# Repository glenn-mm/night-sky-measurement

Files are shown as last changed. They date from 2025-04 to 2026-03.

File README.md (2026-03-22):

# night-sky-measurement
Build and code for optical night sky measurements

Calibration will require the use of an SQM-L device from https://www.unihedron.com/projects/sqm-l/

## Build Steps:
1. Solder the pins onto the QtPy
2. Connect the uFL antenna to the QtPy
3. Connect TSL2591 via STEMMA cable to QtPy
4. Solder the pins onto the display
5. Download Thonny (https://thonny.org)
6. Install Circuit Python onto QtPy via Thonny (put chp into boot mode first!)
7. Download Circuit Python libraries (https://circuitpython.org/libraries)
8. Add necessary libraries to Circuit Python drive under lib directory
   * adafruit_bus_device
   * adafruit_tsl2591.mpy
   * adafruit_displayio_ssd1306.mpy
   * adafruit_ssd1306.mpy
   * adafruit_display_text
9. Run example from https://github.com/adafruit/Adafruit_CircuitPython_TSL2591/blob/main/examples/tsl2591_simpletest.py
10. Copy code.py from this project and test display and sensor
11. Package into case
12. Calibrate
13. Bonus - connection to wifi + adafruit.io

## Build Steps explained:

### Breadboard layout (1)
* This picture shows the nomimal layout of the breadboard to get started
* Start by pressing the QtPy headers into the rows shown and soldering the QtPy to the headers

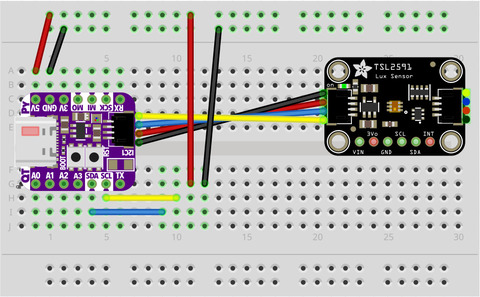
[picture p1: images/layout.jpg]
Fritzing breadboard layout


### QtPy with antenna (2)
* The uFL antenna is tricky to connect and requires a decent amount of force
* After soldering the QtPy to the headers on a breadboard verify the antenna connects

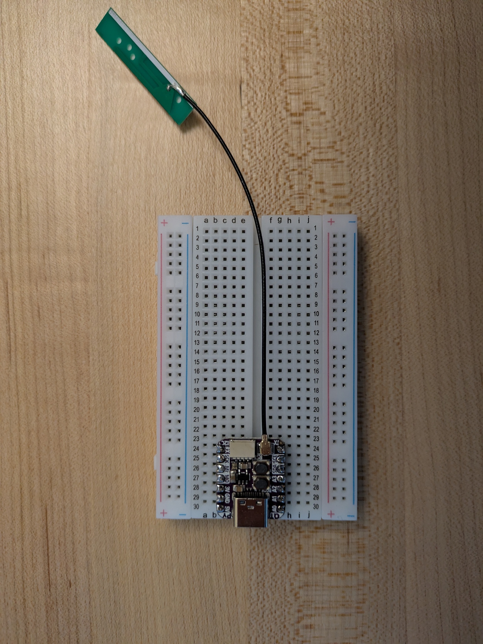
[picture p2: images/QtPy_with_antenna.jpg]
QtPy with antenna


### Attach TSL2591 (3)
* Attach the TSL2591 sensor via the STEMMA QT cable

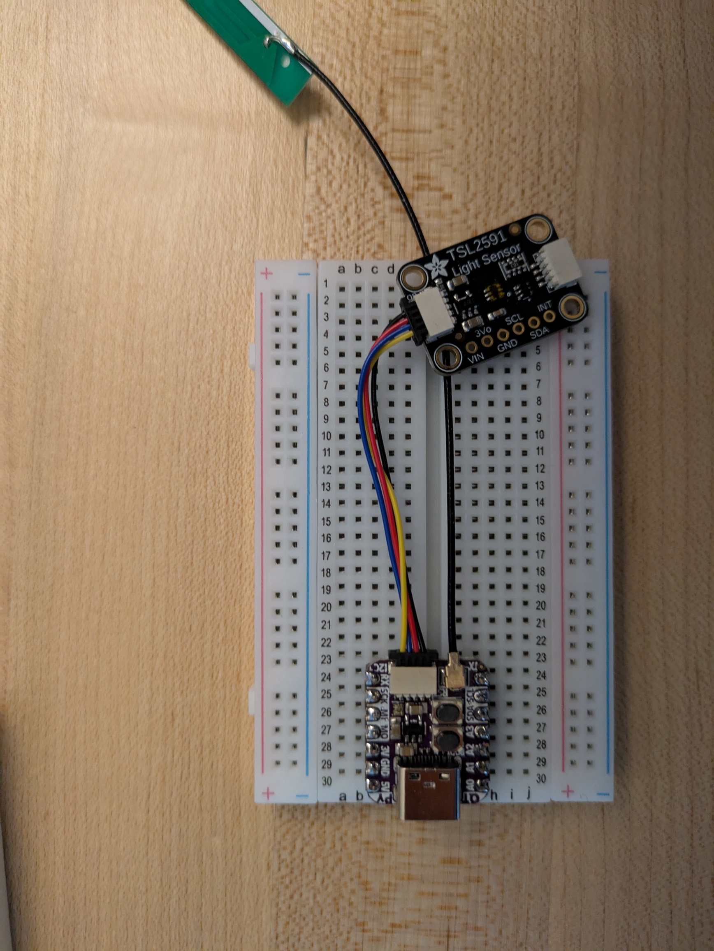
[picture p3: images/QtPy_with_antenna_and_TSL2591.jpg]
QtPy with antenna + TSL2591


### Attach oled display (4)
* Attach the oled display
* Wire the 5V, GND, SCL and SDA over to the oled break out

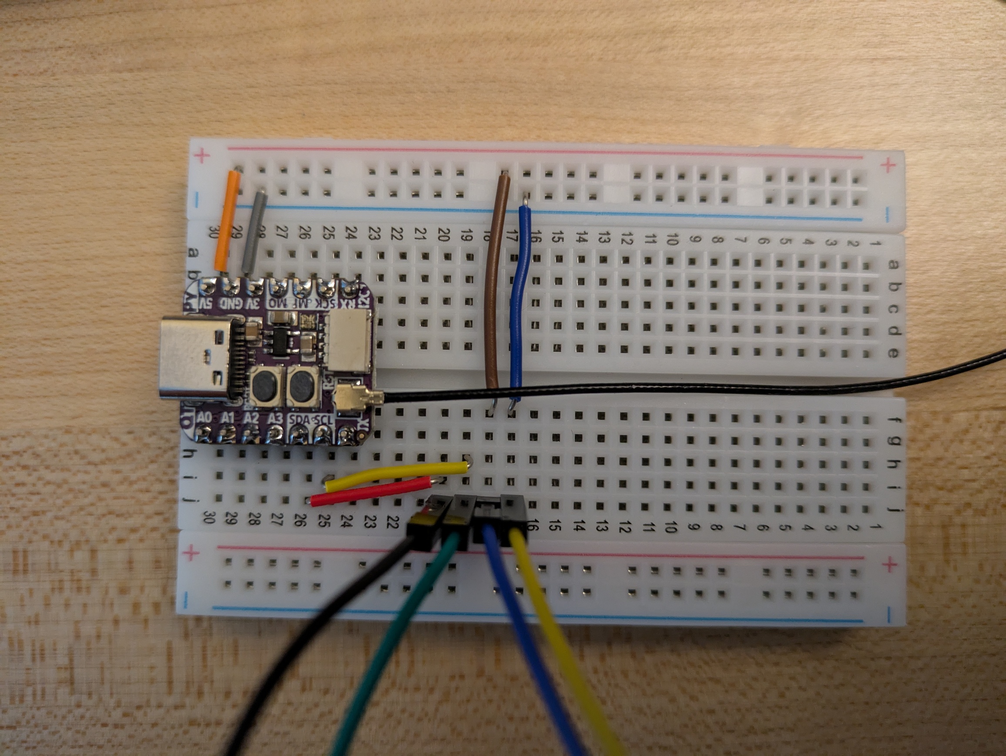
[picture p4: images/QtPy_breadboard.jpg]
Breadboard with oled break out


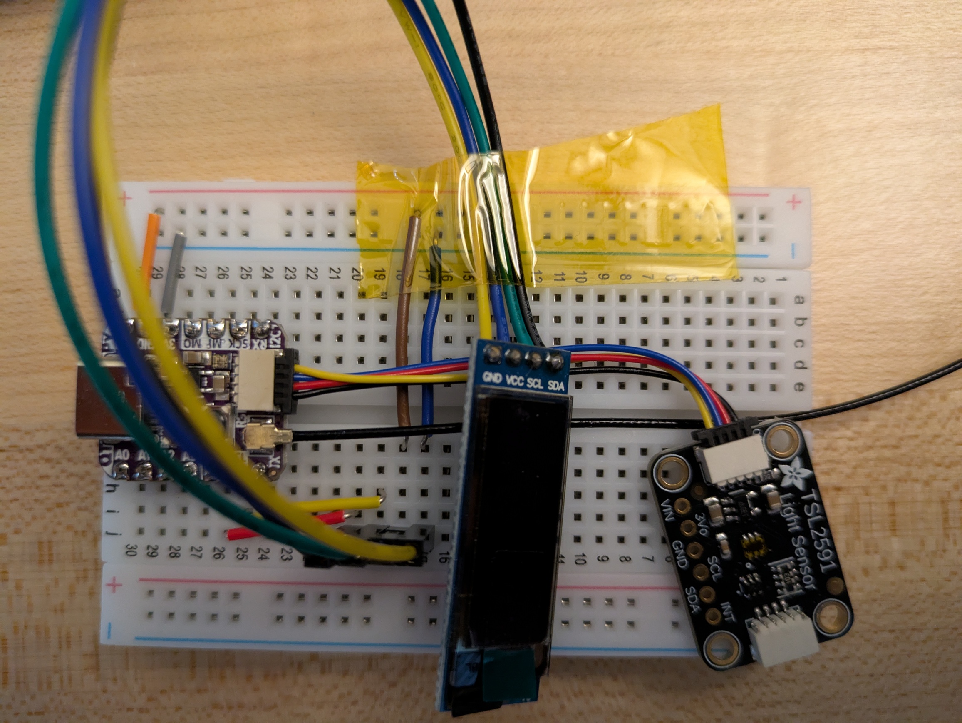
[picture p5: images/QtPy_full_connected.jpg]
Fully connected


### Setup CircuitPython (5-8)
* Download Thonny (https://thonny.org)
* Setup for CircuitPython (set interpreter, see screenshot)

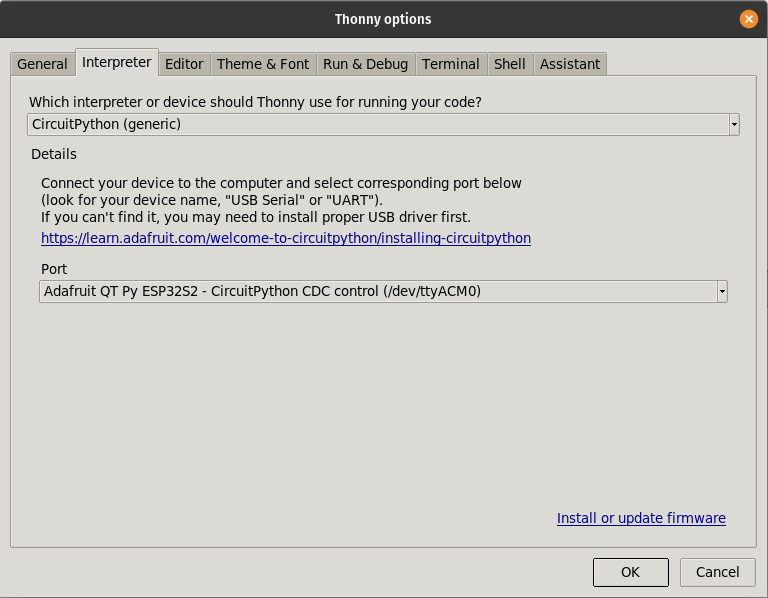
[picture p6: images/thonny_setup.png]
Thonny Python selection


* Update firmware (put chip into boot mode, see screenshot)

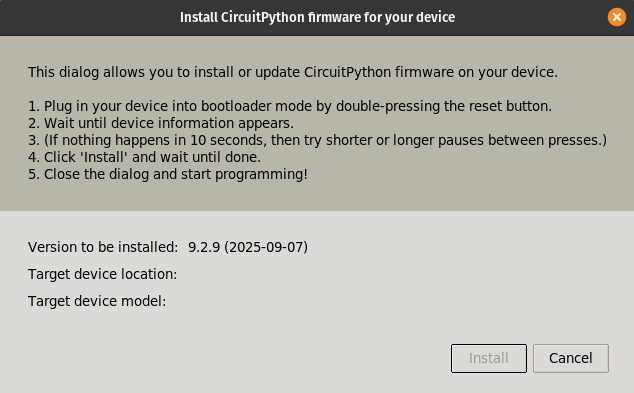
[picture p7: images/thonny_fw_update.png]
Thonny firmware update


* Download Circuit Python libraries (v9) (https://circuitpython.org/libraries)
* Install necesary libraries from Step 8 above
  * Copy files/folders into CIRCUITPY drive while board is plugged into computer

### Run test example
* Download python file from Step 9 (https://github.com/adafruit/Adafruit_CircuitPython_TSL2591/raw/refs/heads/main/examples/tsl2591_simpletest.py)
* Open python file with Thonny
* Run python file with board plugged into computer
  * Look for console output with the Total, Infrared, Visible and Full spectrum measurements
  * Occlude the TSL2591 sensor and ensure values drop in magnitude

### Install/Update code
* Download this project's python code and calibration file into the CIRCUITPY drive
  * Download code.py, display.py, sensory.py and tsl2591_calibration.json into your CIRCUITPY drive
  * CIRCUITPY drive will be in Drives under Windows and /media/$USER/CIRCUITPY under Ubuntu
* (Advanced) See bottom of page for doing your own calibration

### Package the project
* 3D print the [upper](case/case_upper.stl) and [lower](case/case.stl) cases

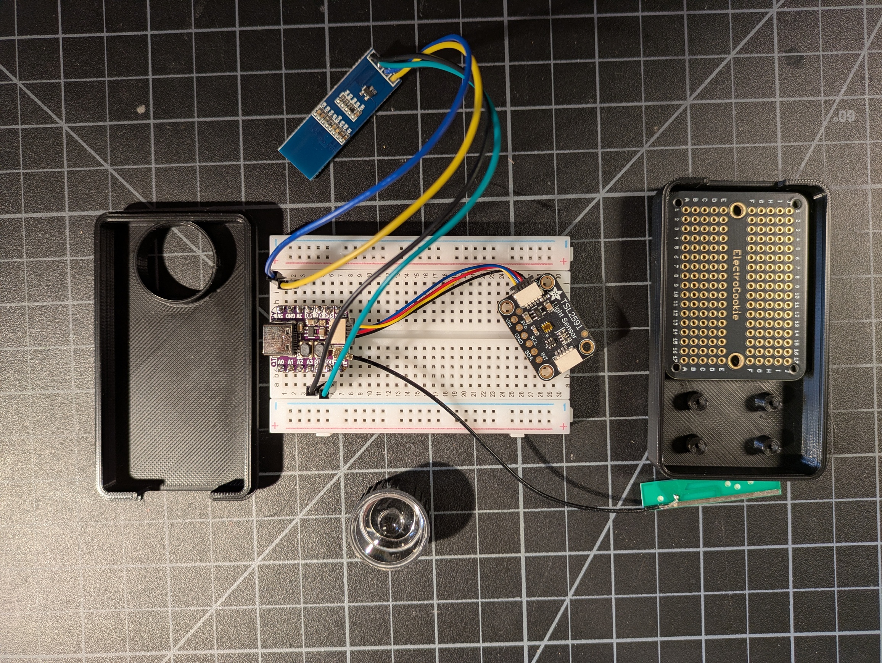
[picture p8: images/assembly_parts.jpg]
Assembly Parts


* Thread the internal posts with the m2 screws (requires a little bit of force)
* Move QtPy onto proto board and solder

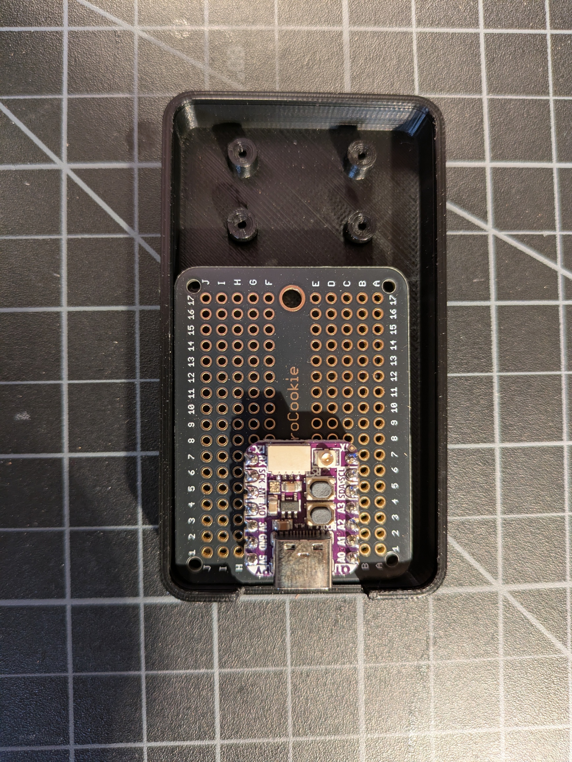
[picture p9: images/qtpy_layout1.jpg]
QtPy Layout


* Solder display wires onto proto board

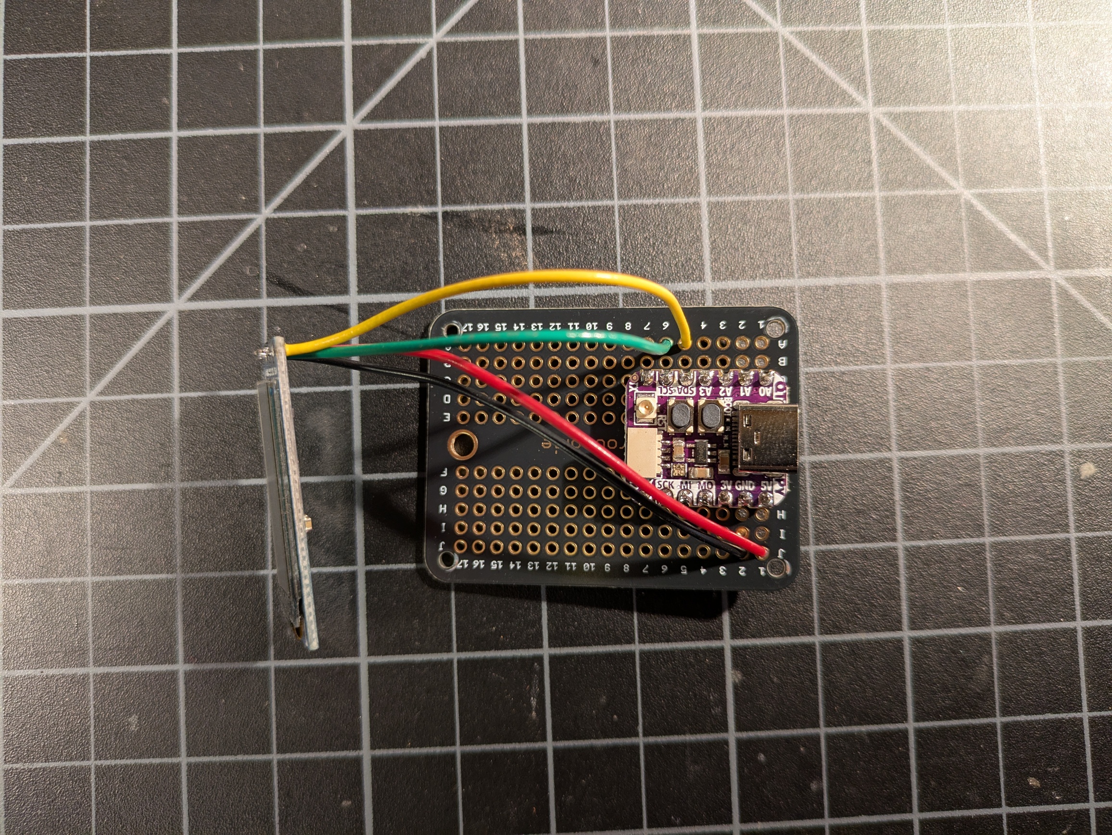
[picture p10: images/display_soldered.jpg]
Display wiring


* Mount sensor and display (ensure display lines up with hole)

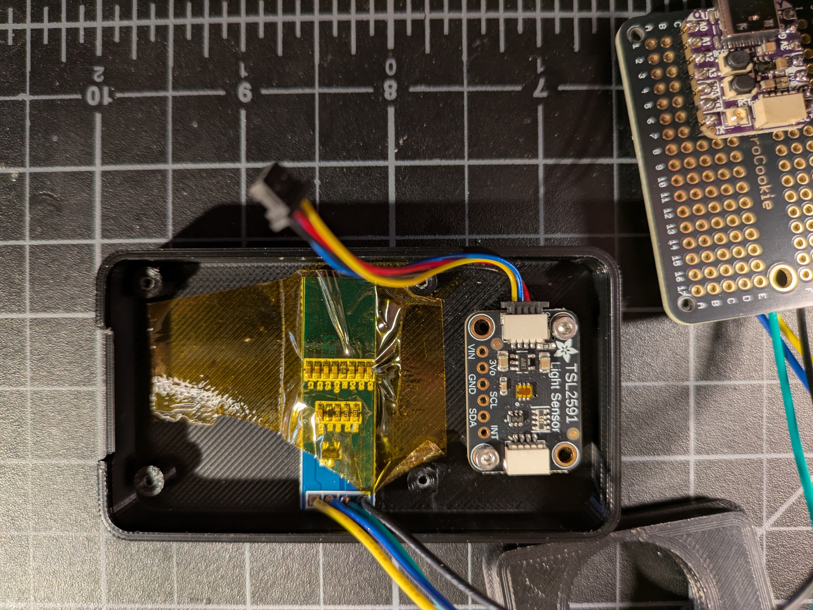
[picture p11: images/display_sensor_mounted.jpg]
Display + TSL2591 in case


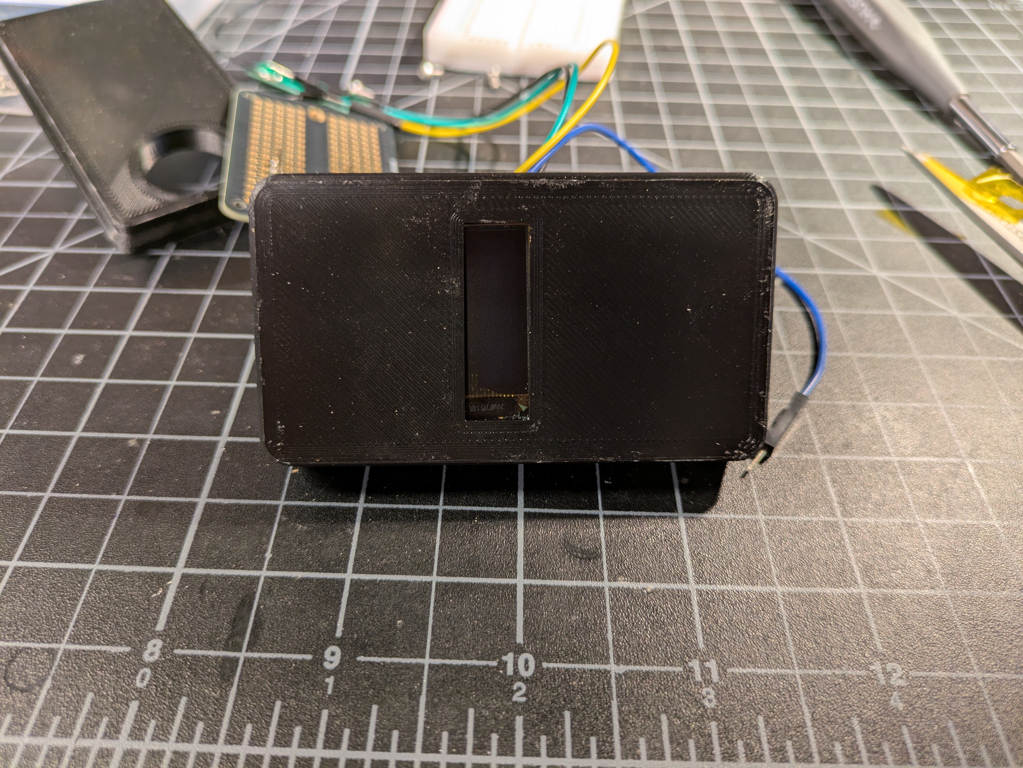
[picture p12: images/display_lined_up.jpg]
Display lined up


* Mount proto board and adhere the antenna

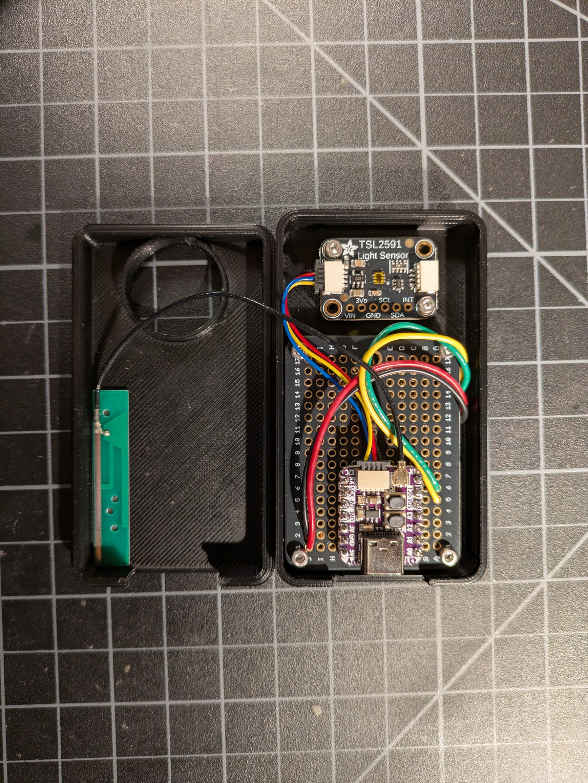
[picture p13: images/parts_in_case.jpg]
Parts in case


* Mask or disable the Green LED on the TSL2591
  * One can use gaffer tape or scratch the LED connection

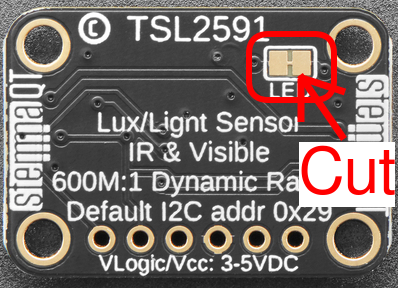
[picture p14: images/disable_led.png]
Disable LED


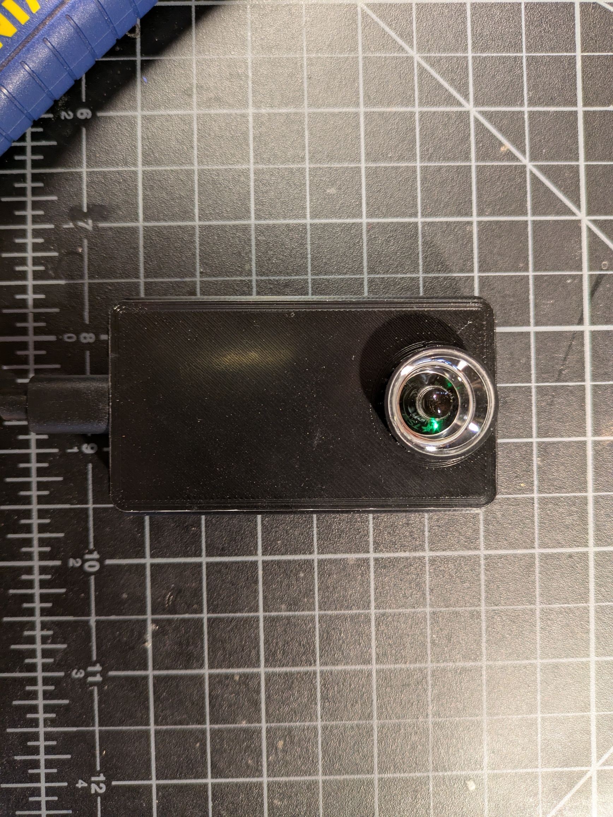
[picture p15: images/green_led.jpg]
Forgot to mask


* Close up the case and install the lens

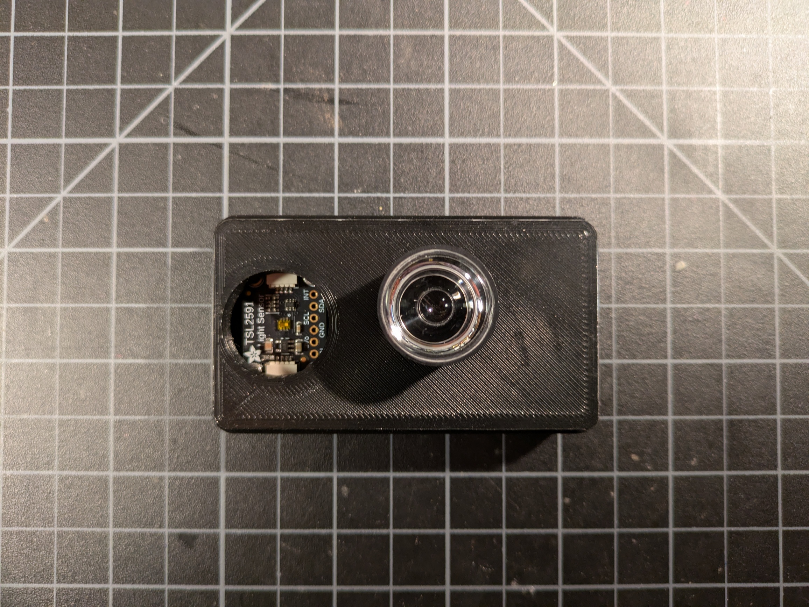
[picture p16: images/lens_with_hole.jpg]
Lens and Case


* Power on and verify working display

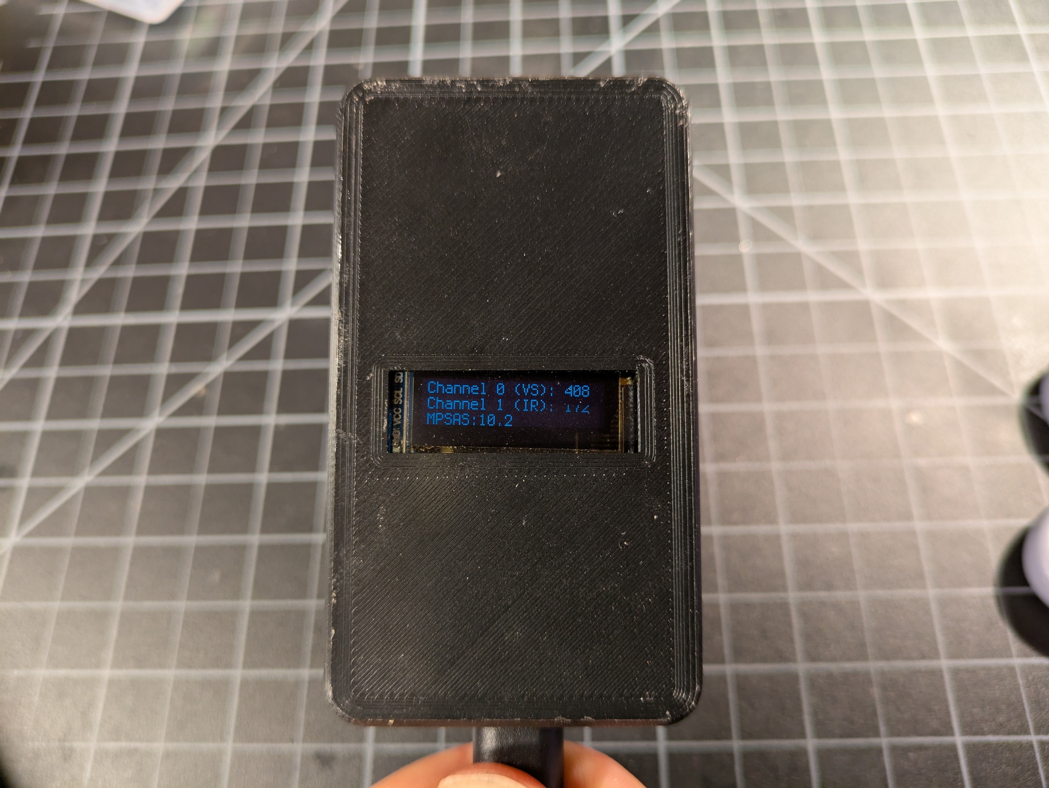
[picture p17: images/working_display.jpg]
Working display and sensor


### Calibration (Advanced)

Note: this requires you have access to a controlled light source and dark room/tunnel as well as an SQM-L device

* Run calibration steps
  * Remove tsl2591_calibration.json from CIRCUITPY directory
  * Start up Thonny
  * Plug in USB
  * Hit Y to begin calibration
    * Unmount CIRCUITPY drive
  * Follow prompts for readings with SQM-L
    * Setup light intensity, take an SQM-L reading, device calibrates
    * Rinse and repeat until done (great light range is better)

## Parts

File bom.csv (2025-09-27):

Part | Description | Quantity | Link
1980 | Adafruit TSL2591 High Dynamic Range Digital Light Sensor - STEMMA QT | 1 | https://www.adafruit.com/product/1980
2308 | 2.4GHz Mini Flexible WiFi Antenna with uFL Connector - 100mm | 1 | https://www.adafruit.com/product/2308
5348 | Adafruit QT Py ESP32-S2 WiFi Dev Board with uFL Antenna Port | 1 | https://www.adafruit.com/product/5348
4399 | STEMMA QT / Qwiic JST SH 4-Pin Cable - 50mm Long | 1 | https://www.adafruit.com/product/4399
n/a | 0.91 Inch I2C IIC OLED Display Module OLED Screen | 1 | https://www.amazon.com/dp/B0BWJLV39P
n/a | ElectroCookie Mini PCB Prototype Board Solderable Breadboard | 1 | https://www.amazon.com/dp/B081MSKJJX
n/a | m2 screws | 9 | TBD

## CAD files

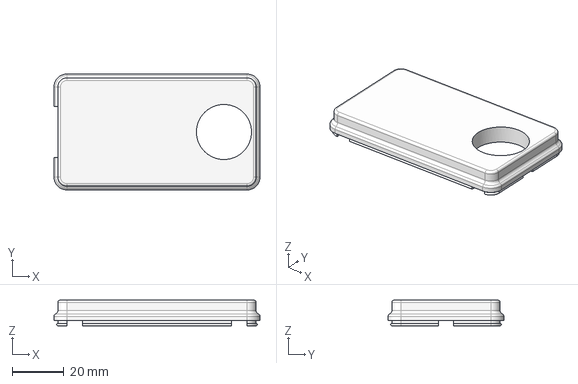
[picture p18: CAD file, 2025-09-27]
case/case_upper.step
80.0 x 45.0 x 10.0 mm

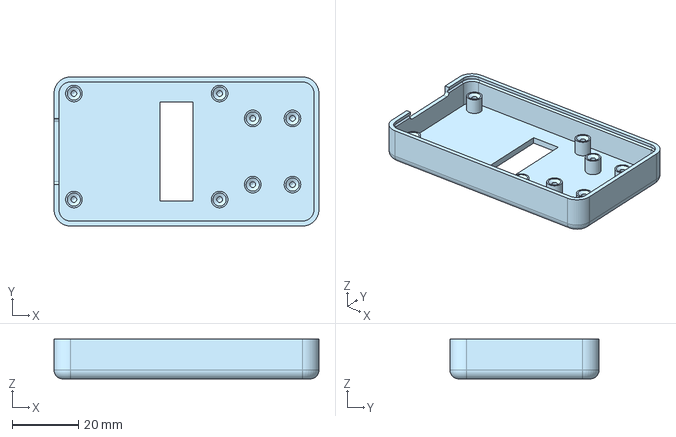
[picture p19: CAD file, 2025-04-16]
case/case.step
80.0 x 45.0 x 12.0 mm

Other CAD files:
case/case.stl

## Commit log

2025-04-16 adding bottom case stl/step for 3d prints and modification
    [case.step, case.stl]
2025-04-16 adding basic bill of materials (sans wires and 3dp parts)
    [bom.csv]
2025-09-27 print out screen outputs
2025-09-27 adding final print
2025-09-27 add ranging integration times and re-read sensor after gain/integration changes to clear
2025-09-27 adding top enclosure for case
    [case_upper.step]
2025-09-27 documentation update for build instructions
    [bom.csv, case.step, case.stl, case_upper.step]
2025-10-05 first cut at adding calibration routines
2025-10-05 fixing parent class calls and calibration storage
2025-10-24 fixing calibration
2025-11-03 adding calibration file
2026-03-22 new calibration data
2026-03-22 rework display for lines, update prints, use mean mpsas
2026-03-22 update readme with calibration and update steps
2026-05-30 fixing print for sensor readings out of range
